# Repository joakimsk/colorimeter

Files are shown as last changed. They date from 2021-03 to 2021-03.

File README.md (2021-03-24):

# Colorimeter

A project to develop an open source colorimeter that is "good enough". End goal is to analyze sample colors for water quality measurements, using off-the-shelf test kits for aquarium water quality. In the process, maybe we can do a sample with less reagents, as well.

Photometer: Measuring quantity of light, usually all kinds of wavelengths, "full spectrum". Output is light intensity.

Colorimeter: Measures the absorbance of particular wavelengths of light by a specific solution. Normally, only a narrow wavelength, where most light is absorbed by the solution, selected with filters is used to maximize accuracy, and Beer-Lambert law is applied to deduce the solution strength.

Spectrophotometer: Measures the absorbance across several wavelengths of light, giving a graph of spectral absorption. Like a colorimeter but across many wavelengths.

I believe this means that we could manage with a single "full-spectrum" light measurement of the liquid, but it gets more accurate as we select correct wavelength. A spectrophotometer is more fancy than necessary in our case.

If our solution will be green to blue, we want a light source that is in between green and blue, depending on where we want best accuracy.

Read the [NOTES.md](NOTES.md) for more details and testing.

## What you need
### Hardware needed
- An LDR, light sensitive resistor as light detector
- A single-wavelength or multi-wavelength LED as light source
- A couvette, preferably of quartz due to its optical qualities (Mine is 12.5x12.5x45mm from Purshee.com wavelength 200-2500nm, 3.5ml volume)
- An Arduino to make the measurements
- A PC to run software and analysis

### Tools needed
- A 3D-printer is nice but not necessary, print in black filament if possible, reduce light noise. Or spray paint with black. Or run in dark room.
- A PC for software
- Basic electronics tools are recommended

### Other things needed
- Food coloring for initial tests (optional)
- Water quality test kit (ammonia suggested, can be of any chemistry, but I am using salicylate method, JBL Seawater Ammonia test kit)
- Household ammonia (to calibrate software)
- A small syringe, I have 1 ml with a short tip from the local pharmacy

## Theory
Send light through a liquid, our sample. Detect how much light is received. With light at a certain color, the light received tells us how much light was absorbed, and how much was passed through the sample. If we use three different colors, maybe we can say which color the liquid is.

By taking samples through time, we can explore the kinematics of the liquid, to make sure we make a reading we can trust, when reagents are done reacting.

Putting this all together, we can also calibrate the readings of the kits to a known solution, for example using an ammonia kit and dosing ammonia at certain concentrations.

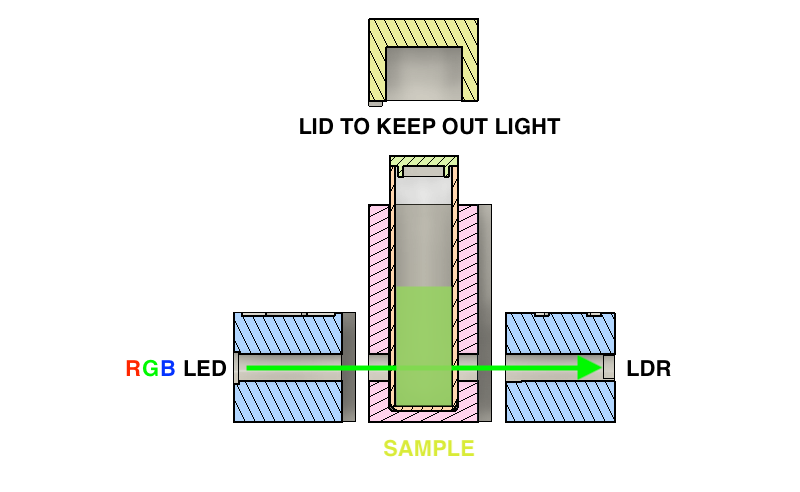
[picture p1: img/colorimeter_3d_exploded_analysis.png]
Light path

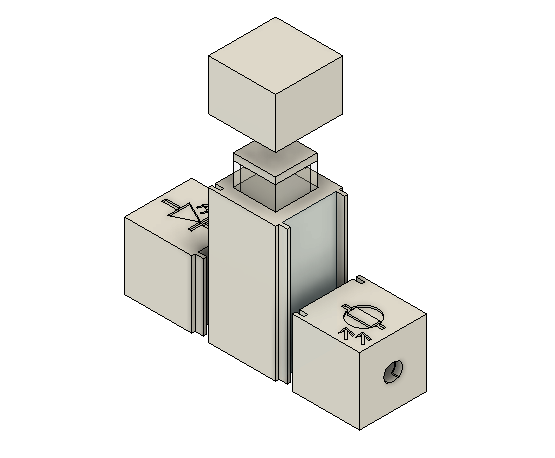
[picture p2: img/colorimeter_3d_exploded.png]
Overview of couvette holder


Something like that.

### Optical parameters
Reflectance: Amount of reflected light, referenced to a reference measurement. Expessed in % or dB, negative number.

Absorbance: Amount of light absorbed, referenced to a reference measurement, can be original light source. Expressed in dB, considered opposite of transmittance.

Transmittance: Amount of light transmitted through a liquid, referenced to a reference measurement, can be original light source. Expressed in % or dB.

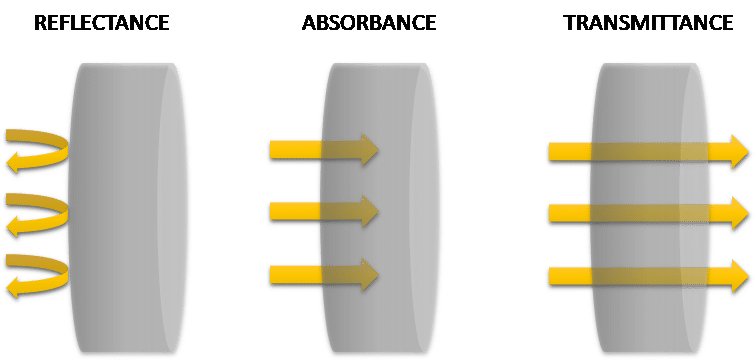
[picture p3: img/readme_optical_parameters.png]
Optical parameters, copyright original owner


[pyroistech.com relative measurements ](https://www.pyroistech.com/relative-measurements/)

We should probably decide on what 100% transmittance is, then do a divison to find relative transmittance for various colors/wavelengths.

[sigmaaldrich.com transmittance/absorbance table](https://www.sigmaaldrich.com/technical-documents/articles/biology/transmittance-to-absorbance.html#:~:text=Absorbance%20(A)%20is%20the%20flip,be%20determined%20using%20this%20calculator.)

### Beer-Lambert law
[wikipedia.org Beer-Lambert law](https://en.wikipedia.org/wiki/Beer%E2%80%93Lambert_law)

Related to the attenuation of light, as it passes through a material. Absorbance = absorpitivity * optical path in cm * concentration of attenuating species.

Should only be applied to absorbance within 0.2 to 0.5, to maintain linearity.

## LDR details
The LDRs are commonly of CdS, Cadmium sulfide. They have also been mostly discontinued on Elfa Distrelec, but I found a datasheet.

They are most sensitive to green wavelengths, which may explain blue and green samples giving nearly the same, high response.

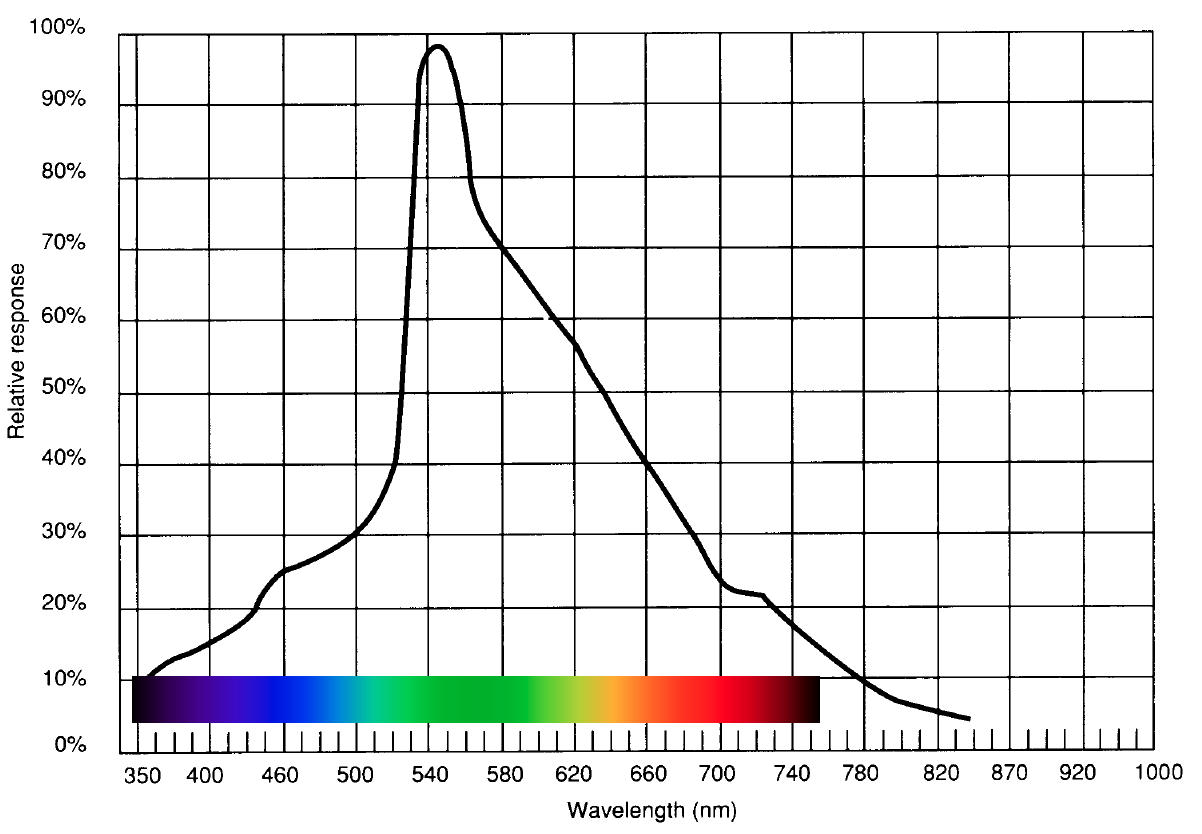
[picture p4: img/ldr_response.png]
LDR spectral response

[pdf: ldr datasheet](pdf/ldr_datasheet.pdf)

## Quartz couvette details
The couvettes are often found in plastic, normal glass and quartz glass. There are various types of quartz, suitable for different wavelengths.

Here is a typical UV Quartz couvette transmittance plot, very transmissive from 200 to 2000 nanometers, far beyond visible light.

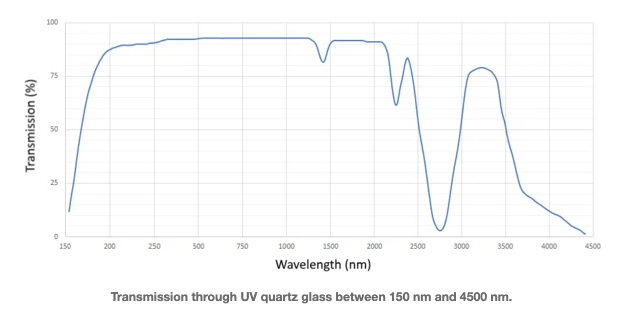
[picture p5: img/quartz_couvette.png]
Quartz couvette Quartz


## Error sources
- If using a round couvette (glass vials that follow test kit), light can get bent along sides and avoid the liquid all-together. Thus we do not use the vials, for now.

- If using a small reagent dose, we may get imbalance in chemistry. Not sure how this will affect the reading. Read up on best practice with syringe usage.

- White PLA plastic, and 20% infill during print will allow more light to pass through the body. And, imperfect joints will too. Try black plastic spray paint for this. If not enough, use black PLA and set 100% infill. If still not enough, put it all inside another light-proof box.

- LDR and LED may not be accurate enough, so we may consider upgrading these components, maybe using a light sensor instead of a light resistor. LDR resistance is among other, temperature dependent. LDR has also a bit of latency, it takes time for the resistance to reach stable value, going from full dark to full light, often taking one second.

- Conversion roundoff errors and noise in Arduino may become a problem as well. Arduino Uno is 8 bit, the ADC has 8 bit resolution. The LDR is an analog device.

- Temporal issues due to sampling not being instant - if we make several readings at several colors, these will necessarily happen at a delta t larger than 0. Meaning that our readings will not happen in the same time, but spread over time, giving us small errors. By making sampling faster, we can mitigate but not eliminate this. Using a full spectrum light and read all wavelengths at the same time would be the best, but most expensive.

## Remaining work
- ~~Design 3D models, then print for couvette-assembly~~
- ~~Assemble electronics~~
- ~~Make Arduino software~~
- Make PC software (in progress)
- Test and calibrate (in progress)
- Final casing

## Final thoughts
The idea of the colorimeter works well, but there are some numbers of improvements I suggest for the future.

- The LDR is undocumented, and delays the whole sampling process, since it takes time for it to settle when light exposure changes. Get a phototransistor or a color sensor or similar.
- The RGB led is undocumented as well as lacking a "full spectrum" white color. Preferably it is replaced with well documented light sources, or as in professional instruments, with color filters on a natural light source.
- The 3D-printed casing should be printed in black plastic, fully filled, to avoid light leakage.
- The modularity is not necessary, so consider printing it all in one print.
- The quartz couvette is overkill, it seems, can potentially manage well with normal glass couvettes, or even plastic, due to calibration.
- The arduino programmed as a simple device works well, with program logic in python.
- The color standards should be more standard, food coloring works to get an impression but it still do not seem very standard, at least not without measuring exactly. Also, maybe we do not need standards anyhow, after designing this system.
- There should be a couvette holder nearby, at all times, to avoid spilling water all over the place. I suggest printing this as an addon.
- Using wood as a base works well, with glue gun to keep things together.
- Using a small couvette with lesser volume makes you depend on an exact syringe - get an exact robust syringe, not cheap one that loose its markings over time.
- Making one that fits aquarium test vials may be nice, one for JBL, one for 

## Theory & code references
[moleculardevices.com Absorbance](https://www.moleculardevices.com/technology/absorbance)
[electronics-tutorials.ws Light sensors](https://www.electronics-tutorials.ws/io/io_4.html)

## Similar work
[mit.edu Low Cost Colorimeter](http://www.mit.edu/~milesdai/projects/colorimeter/index.html)
[iorodeo.com Open Source Colorimeter Project](https://iorodeo.com/pages/colorimeter-project)
[instructables.com Inexpensive photometer & colorimeter](https://www.instructables.com/An-Inexpensive-Photometer-and-Colorimeter/)
[arduino.cc Open Source Colorimeter](https://create.arduino.cc/projecthub/MOST/open-source-colorimeter-cd0a76)
[arduino.cc Mini spectrophotometer](https://create.arduino.cc/projecthub/radsensors/minispec-0e3bc5)
[publicLab.org Desktop spectrometer with DVD diffraction grating](https://publiclab.org/notes/abdul/08-11-2016/constructing-a-desktop-spectrometer-with-no-wood-and-no-velcro)

[researchgate.net A Simple, Rapid Analysis, Portable, Low-cost, and Arduino-based Spectrophotometer with White LED as a Light Source for Analyzing Solution Concentration](https://www.researchgate.net/publication/324161531_A_Simple_Rapid_Analysis_Portable_Low-cost_and_Arduino-based_Spectrophotometer_with_White_LED_as_a_Light_Source_for_Analyzing_Solution_Concentration)
[researchgate.net Open-Source Colorimeter](https://www.researchgate.net/publication/236252679_Open-Source_Colorimeter/link/0c9605171839574c56000000/download)
[iop.org Development of color detector using colorimetry system with
photodiode sensor for food dye determination application](https://iopscience.iop.org/article/10.1088/1742-6596/1185/1/012031/pdf)

## Possible light sources and detectors
[sparkfun rgb light sensor ISL29125](https://www.sparkfun.com/products/12829)
[Digital 16bit Serial Output Type Ambient Light Sensor IC BH1750FVI](https://www.mouser.com/datasheet/2/348/bh1750fvi-e-186247.pdf)
[electronics-notes.com LDR: Light Dependent Resistor](https://www.electronics-notes.com/articles/electronic_components/resistors/light-dependent-resistor-ldr.php)

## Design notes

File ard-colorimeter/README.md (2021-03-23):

# ard-colorimeter
Arduino program to interface with colorimeter

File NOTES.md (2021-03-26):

# Colorimeter Notes
## PWM vs LDR resistance

Measurement of LDR resistance against PWM output value, Arduino ADC range is {0-255}. Shining through the colorimeter, but without couvette (i forgot it...).
Colorimeter is kept in the dark (with a Norwegian dark grey lue), so light pollution should be minimal.

|       	| 20     	| 45    	| 50    	| 100  	| 150  	| 200  	| 250  	| 255  	|
|-------	|--------	|-------	|-------	|------	|------	|------	|------	|------	|
| Red   	| ~1975k 	| ~835k 	| ~760k 	| 366k 	| 241k 	| 180k 	| 144k 	| 142k 	|
| Green 	| 526k   	| 232k  	| 208k  	| 102k 	| 67k  	| 49k  	| 38k  	| 38k  	|
| Blue  	| ~760k  	| 333k  	| 299k  	| 141k 	| 88k  	| 63k  	| 49k  	| 48k  	|
| All   	| 249k   	| 112k  	| 101k  	| 50k  	| 32k  	| 23k  	| 18k  	| 18k  	|

All means all three colors are turned on at the same time. Driving voltage is 5v, and resistors I forgot to write down...

We do this to consider which resistor value to use for the voltage divider on the LDR side.

We also get an impression of where the LDR is most sensitive, and least sensitive.

Here is a chart of the data.

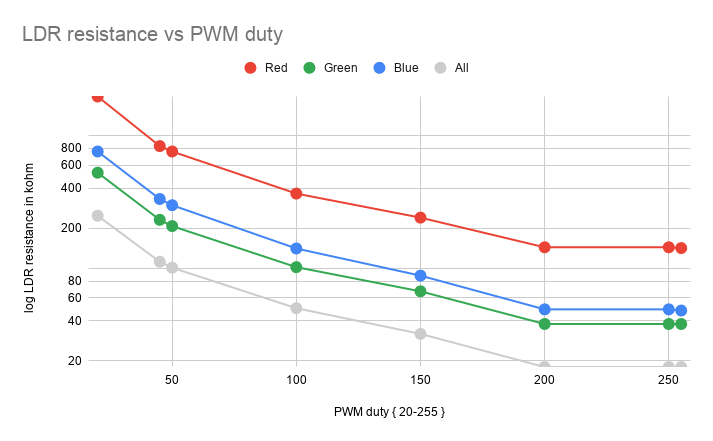
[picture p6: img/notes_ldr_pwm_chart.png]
Light path LDR vs PWM duty chart


Average of the table is 256.9 kohm
Median of the table is 126.5 kohm

I cannot remember how to select optimal value, so I will just use the average value as the second resistor in the voltage divider. This should give us a 2.5 volt to ADC when the LDR is at the average value.

I select 220 kohm + 38.6 kohm, measured to 258 kohm, near enough to 256.9 kohm.

We set RGB to <100,100,100>
LDR resistance with clear path: 53 kohm
LDR resistance with quartz couvette: 58.3 kohm and inserted wrongly: 191 kohm
LDR resistance with plastic couvette: 61 kohm and inserted wrongly: 66 kohm

## Thoughts about Arduino ADC
The Analog to Digital conversion in the Arduino Uno, using the ATmega328 8-bit MCU, has 10 bits resolution.

ADC Resolution = Vref / ((2^n) - 1) = 5 / ((2^10)-1) = 5/1023 = 0.00488758553 volt bins

Digital output = Vin / Resolution
Digital output = 5 / 0.00488758553 = 1023 (when Vin is 5v)
Digital output = 2.5 / 0.00488758553 = 512 (when Vin is 2.5v)

A voltage divider:
Vout = ( R2 / (R1 + R2)) * Vin
Vout = ( R2 / (R1 + R2)) * Vin

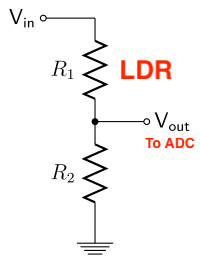
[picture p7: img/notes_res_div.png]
Light path Resistive divider


Setting R2 = 258 kohm
We have R1 being the LDR, varying from 18 kohm to up to 2000 kohm (guestimates finger in the air values from the table).

We set R1 to be LDR because when LDR gets light on it, it will "pull up" Vout to Vin voltage. This is because LDR resistance goes down when light amount goes up.

This gives us two extremes, for high light and low light conditions, remembering that the LDR lowers resistance under higher light:

Vout = ( 258000 / (18000 + 258000)) * 5 = 4.67391304348 volts

Digital output = 4.67391304348 / 0.00488758553 = 956 (when Vin is 5v)

Vout = (258000 / (2000000 + 258000)) * 5 = 0.5713020372 volts

Digital output = 0.5713020372 / 0.00488758553 = 117 (when Vin is 5v)

## Color sample solutions
Food coloring was used to make "standard" solutions for red, green and blue. The primary colors we are interested in, for the Salicylate method for total ammonia nitrogen, is green/yellow to dark blue, but it is nice to check the colorimeter for more colors.

"1 cm long" string of blue food coloring and 5 ml freshwater was mixed.
Aproximately the same amount of red and green was added to their own 5 ml freshwater, and was mixed.

Two "1ml syringes" of colored liquid was added to the quartz couvettes, totalling 2 ml in each couvette, hopefully enough to not allow light to pass in air above the liquid.

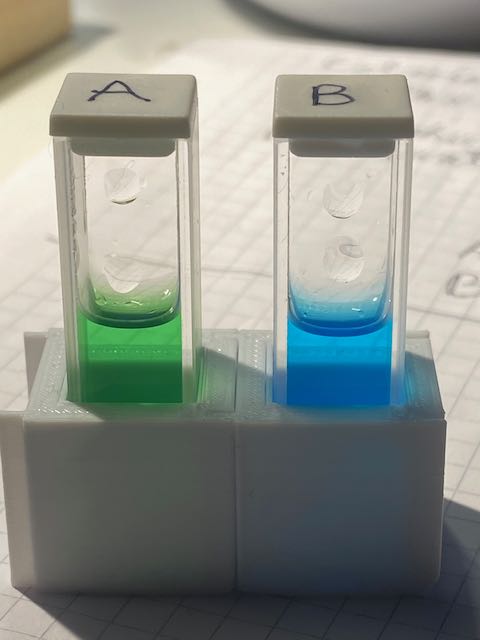
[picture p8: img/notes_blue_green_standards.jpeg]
Blue & Green Blue & Green Standard

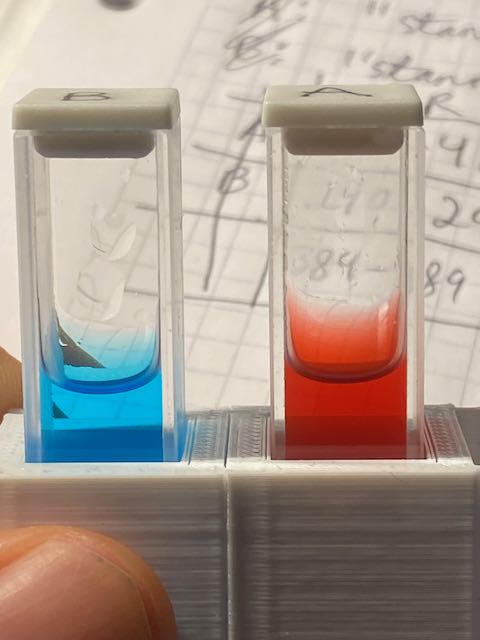
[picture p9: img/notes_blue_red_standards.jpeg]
Blue & Red Blue & Red Standard


## Actual LED colors
It seems that R + G + B != White with an RGB led, to my eyes it looks more azure blue than anything else.
Ideally I would do all this with a white LED as well one day.

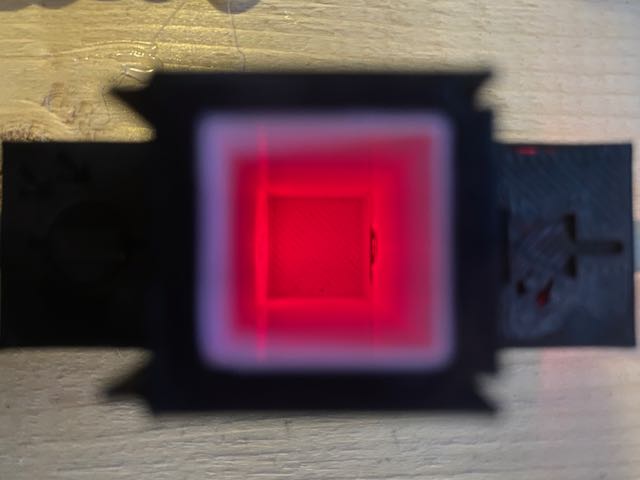
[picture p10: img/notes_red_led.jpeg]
Red Red led

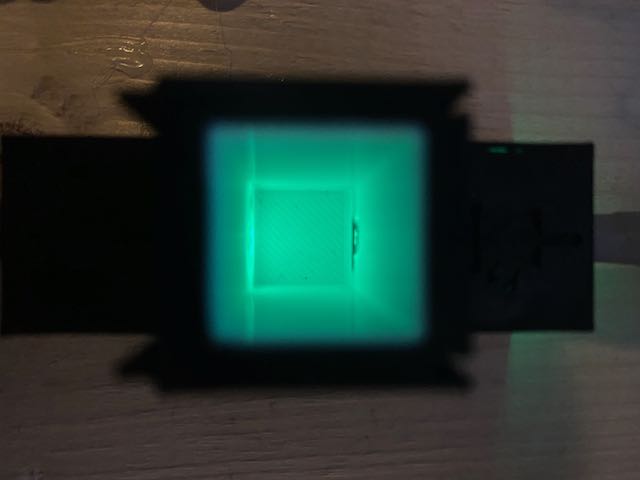
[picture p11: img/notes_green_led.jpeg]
Green Green led

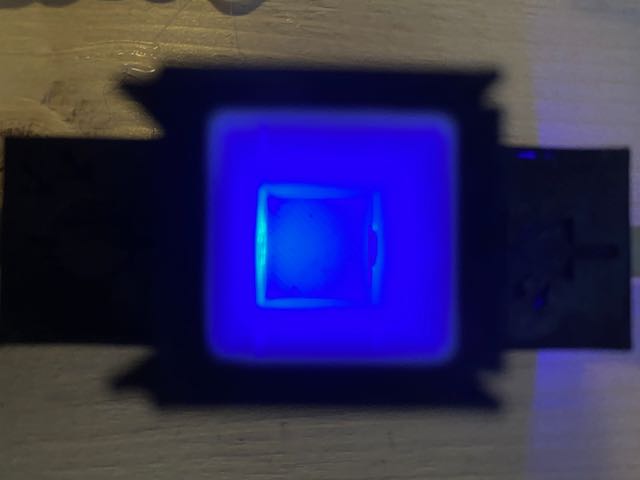
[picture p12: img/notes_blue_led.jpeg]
Blue Blue led

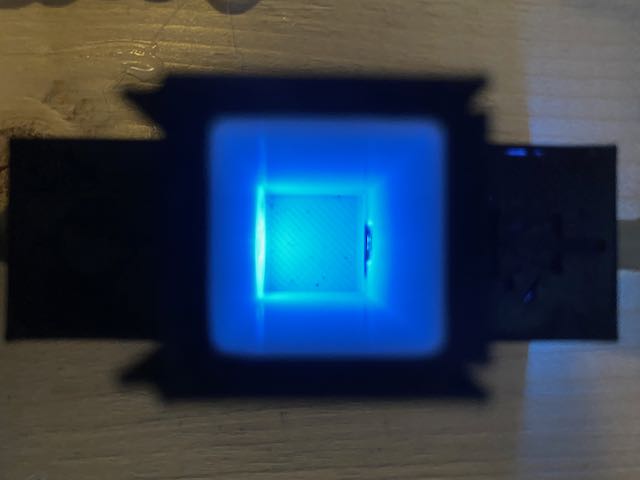
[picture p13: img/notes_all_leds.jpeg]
All All leds


## First trials
We receive the voltage coming from the voltage bridge, using an ADC in the Ardunio, translating this voltage into a value between 0-1023.

We use the "Lue" to make sure its dark around the colorimeter, as the black spray paint was not enough to make it opaque to outside light.

This is just to get to know the thing. Lids of couvettes were marked A and B, to keep them seperate. A couvette stand was used after the first spill of saltwater across the desk.

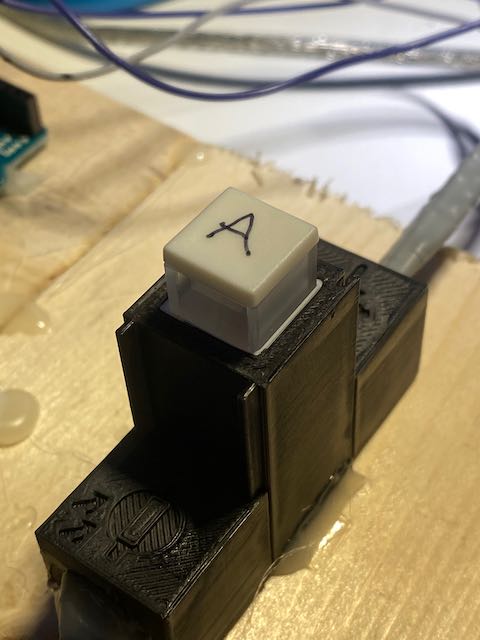
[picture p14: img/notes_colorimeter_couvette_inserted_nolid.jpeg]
Colorimeter, couvette inserted


### Comparing freshwater and saltwater without and with lue
Temperature on both water was roughly 10 degree Celsius in this case. I forgot to make readings with all LEDs on.

Unit: 10-bit ADC values, higher means more light passed liquid
|                  | R       | G       | B       | All |
|------------------|---------|---------|---------|-----|
| Freshwater       | 706-710 | 909-910 | 885-886 | NA  |
| Saltwater        | 703-704 | 906-907 | 882-883 | NA  |
| Freshwater (Lue) | 705-708 | 907-909 | 882-883 | NA  |
| Saltwater (Lue)  | 705-707 | 906-907 | 881-882 | NA  |

Here I wanted to see if Lue had much to say on the readings. It has 1-4 values to say, it seems, so we continue using Lue.
I also think freshwater and saltwater has different colors, but the readings fluctuate a bit so not so easy to say.

### Comparing "standard" freshwater solutions
The "standards" were compared.

Unit: 10-bit ADC values, higher means more light passed liquid
|                    | R       | G       | B       | ALL     |
|--------------------|---------|---------|---------|---------|
| "Standard green"   | 408-412 | 869-870 | 550-553 | 900-902 |
| "Standard blue"    | 290-294 | 891-892 | 879-880 | 950     |
| "Standard red"     | 384-389 | 0-1     | 0-1     | 373-376 |
| "50% standard red" | 566-568 | 48-51   | 141-145 | 612-614 |

It seems that the "standard red" is too dense, it does not allow any green nor blue through it. After diluting 50%, it was better, but still very strong. I believe the standard was mixed too strong.

Here is blue, red and 50% red standards, notice transparency and lack thereof.

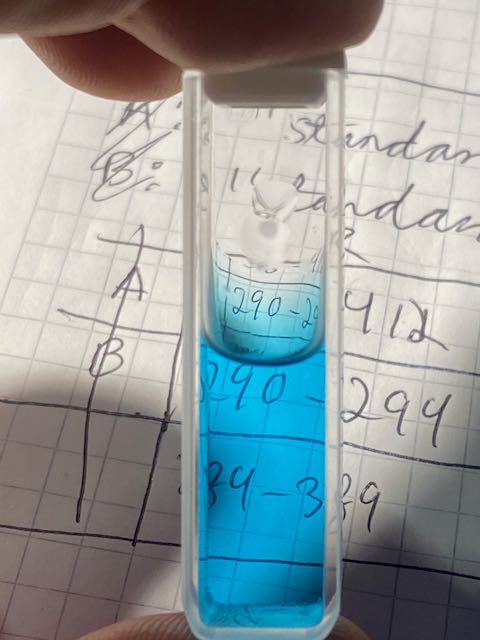
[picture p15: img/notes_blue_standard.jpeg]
Blue standard

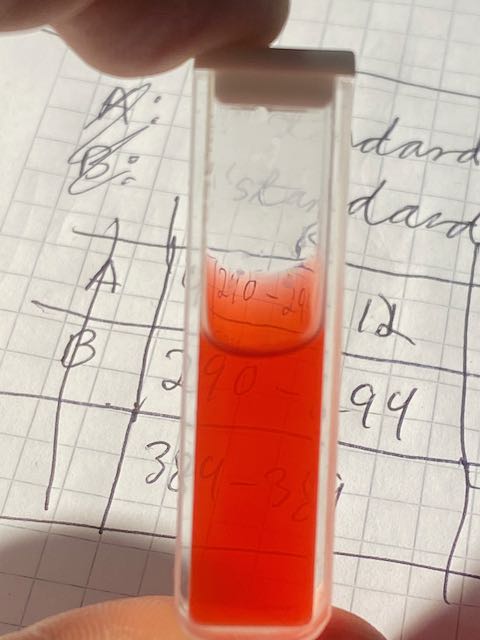
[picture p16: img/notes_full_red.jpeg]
Red standard

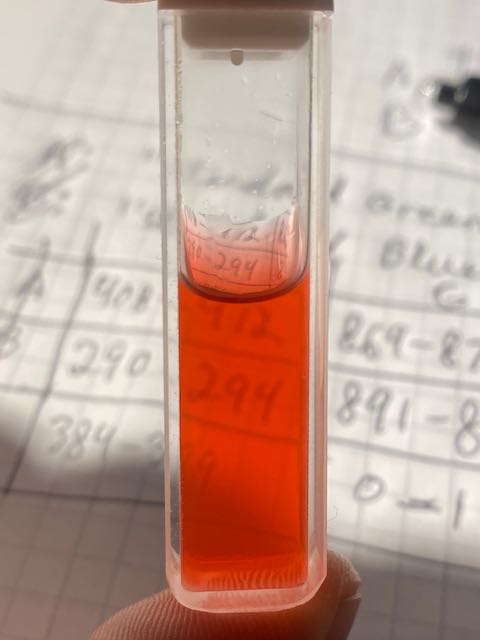
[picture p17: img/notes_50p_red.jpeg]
50% red standard


### Some observations, possible issues and improvements
There is a big difference in viscosity between red, green and blue food coloring. The blue was very viscous, and it was difficult to portion out the amount of coloring by volume

When sampling, I would say I used "n=5-10" by making several reads after a few seconds, when LDR should be stable, not so scientific.

Saltwater vial also had small bubbles in it, which may reduce light. And, try to avoid touching the quartz with my fatty fingers.
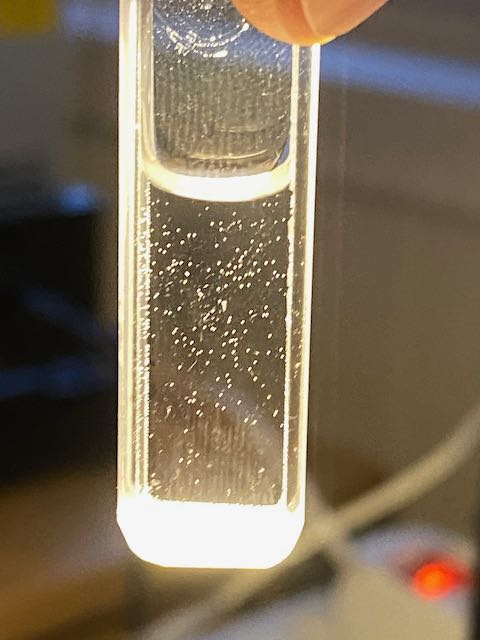
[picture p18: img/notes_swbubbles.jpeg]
Bubbles in saltwater


Pharmacy syringes seem to loose their markings after some mechanical action. Get a proper one.

The LDR likely does not behave linearly, either.

The voltage divider would probably be nicer with a potentiometer, so we can adjust the voltage range.

### Conclusion from first trials
Red is more opaque to green and blue, than red light.
Green is more opaque to blue and red, than green light.
Blue is more opaque to green and red, than blue light.

Could we use ALL leds without a couvette as 100% Transmittance, and then do a simple divison to find transmittance in %? Plausible way forward.
We could also do transmittance at different wavelengths.

## Transmittance implementation
I think we can do this naively, take a calibration reading with an empty couvette in the colorimeter.

Then, take another with the couvette filled with sample liquid, and do a division of ADC values. Output in % transmittance, according to the different LED colors.

Since we do a calibration reading, we should even be able to let the Lue be on the head, where it belongs, instead of on top of the colorimeter.

## LDR time stability and settling-time
It seems that one second is not enough for the LDR to settle after being illuminated. I should probably try an experiment for each LED, to see how long the LDR really takes.

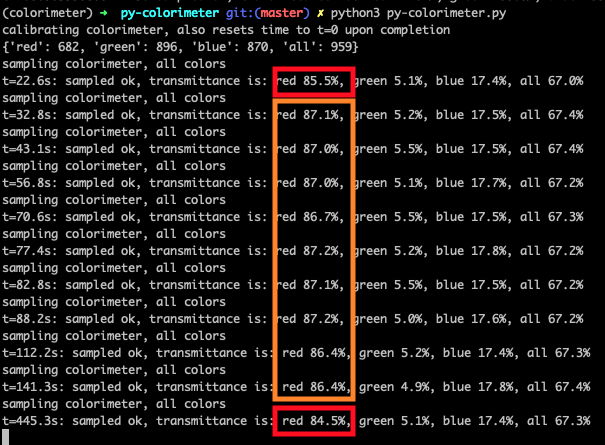
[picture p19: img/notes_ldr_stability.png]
LDR time stability


Notice that after the LDR has been kept in the dark for a while, the end-point does not seem to be reached, since the red-transmittance reading is lower.

Since my LDR is a generic no-name without a datasheet, I have no clue about its spectral response nor its response time, but response time could be deduced experimentally.
My RGB led is also generic no-name, without a datasheet.

[lednique.com ldr details](http://lednique.com/opto-isolators-2/light-dependent-resistor-ldr/)

## Test methods

There are a few different methods, and variations of those used to measure total ammonia nitrogen, TAN, in aquaculture. The goal is to figure out if we have toxic levels of unionized ammonia NH3 in the water, but the test kits have a tendency to be ambigous regarding what they are actually indicating.

Two of the more common ones in the hobbyist aquarium world is:

The Salicylate method. In the salicylate method, monochloramine formed by the reaction of ammonia and hydrochlorine reacts with salicylate to form blue-green colored 5-aminosalicylate in proportion to the amount of ammoniacal nitrogen. Works well on lower concentrations of TAN, commonly 0–1.0 mg/L.

The Nessler method. A combination of mercury (II) iodide and potassium iodide in highly alkaline solution. Gives a yellow color. Contains mercury, and is thus not available in Norway. Also has a wider effective undiluted range of 0.02–5.0 TAN.

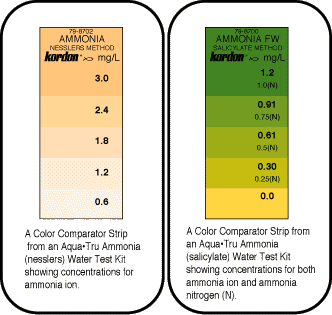
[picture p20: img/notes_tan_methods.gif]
Salicylate vs Nessler

Read more about these two [here](https://aquabaz.tripod.com/ammoniageneral.htm)

And a more detailed comparison of several methods [Comparison of Nessler, phenate, salicylate and ion selective electrode procedures for determination of total ammonia nitrogen in aquaculture](https://www.sciencedirect.com/science/article/abs/pii/S0044848615301058)

On the topic of units, Nofima has a nice writeup in Norwegian. [Here](https://www.nofima.no/filearchive/produksjon-og-giftighet-av-ammoniakk.pdf)

TAN = NH3-N + NH4+-N

Total Ammoniacal Nitrogen = Ammonia-Nitrogen + Ammonium-Nitrogen

This means we are looking at the ammount of nitrogen.

These two parts of TAN exists in a pH-related equilibrium.

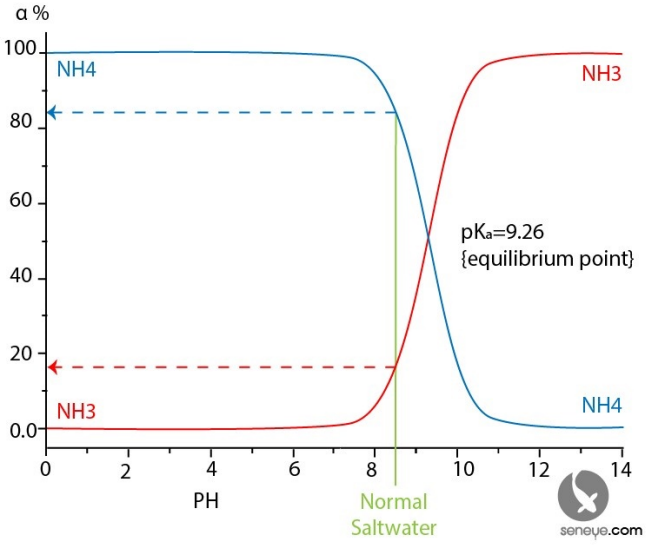
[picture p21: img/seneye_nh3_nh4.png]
NH3 vs NH4


In RAS operating range, we may find pH from 7 to about 8.1, normal seawater.

Calculate Free Ammonia using [Hamza Reef Free Ammonia calculator](https://www.hamzasreef.com/Contents/Calculators/FreeAmmonia.php)

You can also see the [nitrogen-ion conversion chart](https://www.hamzasreef.com/Contents/Calculators/NitrogenIonConversion.php)

## JBL NH4 test kit
The JBL NH4 test kit is used for measuring ionized NH4+, or so they say. I think they actually indicate TAN. The values are indicated to be mg/l or ppm, ranging from below 0.05 to 5.

The chemistry used in this is the Salicylate method, which means the colors we will see range from a light green to dark blue, depending on the ammonia concentration.

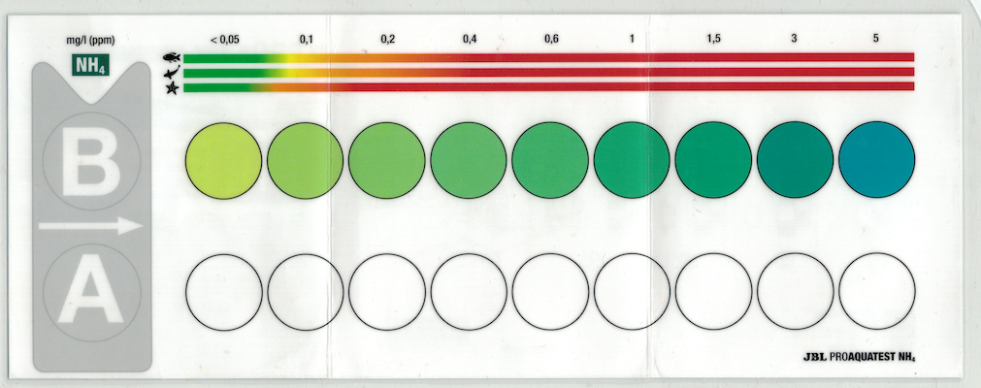
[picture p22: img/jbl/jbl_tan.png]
JBL TAN color sheet


Indicated colors are of the following "NH4", or I believe, TAN.
| Concentrations: 	| <0.05 	| 0.1 	| 0.2 	| 0.4 	| 0.6 	| 1 	| 1.5 	| 3 	| 5 	|
|-----------------	|-------	|-----	|-----	|-----	|-----	|---	|-----	|---	|---	|

The price is roughly 200 NOK, and you get 50 tests out of it if you follow the normal procedure.

The normal procedure is:
1. Add 5 ml water to be measured to a vial
2. Add 4x drops of Solution #1
3. Add 4x drops of Solution #2
4. Add 5x drops of Solution #3
5. Wait 15 minutes, for reaction to take place
6. Compare color of liquid to color indicated on test sheet

Remember that when we measure TAN, we have no idea how much is of the toxic unionized NH3 and how much is of the less toxic ionized NH4+.
To figure out this, we also need to look at the pH and possibly salinity and temperature as well, 

## Ammonia solutions

In order to test our colorimeter, with the JBL NH4 test kit, we need to make a few standard solutions.

We have 9% NH4Cl, Ammonium Chloride, unperfumed from the store.

For 100 liters of water, elevating it from 0 to 1 mg/L TAN, using 9% Ammonium Chloride, and a (calculator)[http://spec-tanks.com/ammonia-calculator-aquariums/].

We need to add 1.1 ml Ammonium Chloride solution.

This is for 1 liter of water, 0.011 ml Ammonium Chloride, too little for me to measure with my 1 ml syringe.

We can take a bucket of 20 liter, add 0.2 ml Ammonium Chloride and get a 1 mg/L solution.
We can take a bucket of 20 liter, add 1.1 ml  ml Ammonium Chloride and get a 5 mg/L solution.

We should also dilute us down to a few different ones.

I have 1 mg/L solution on hand, so I use this and make one more at 0.5 mg/L, by mixing 50/50 of water and solution.

To do later: Make a more complete table, so that we can make better tests.

## TAN kinetics

I put together autosampling, interval of 30 seconds, for 15 minutes. First tests with the real JBL TAN test kit.

Seawater of 1 mg/L TAN, at room temperature (ca 20 degree Celsius):
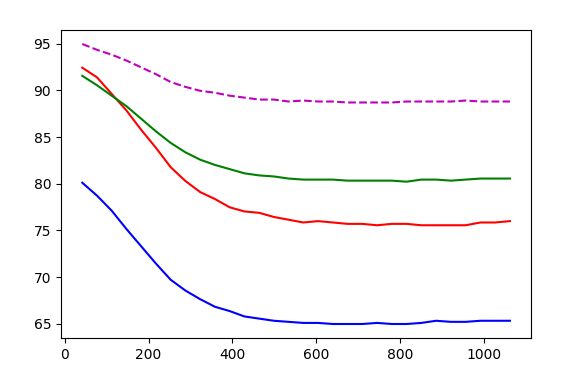
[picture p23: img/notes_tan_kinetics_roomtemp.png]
TAN kinetics room temp


Seawater of 1 mg/L TAN, at fridge temperature (ca 4 degree Celsius):
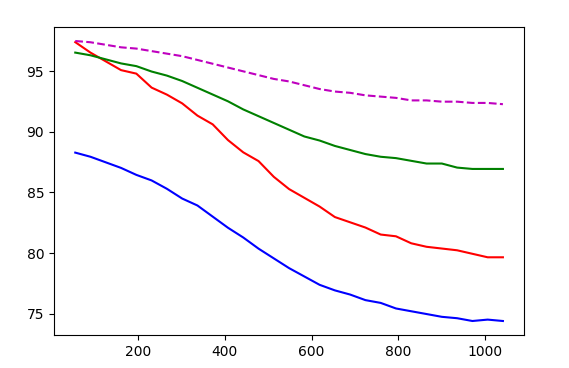
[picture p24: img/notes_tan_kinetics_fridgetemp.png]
TAN kinetics fridge temp


Seeing these side by side, we can clearly see that the cold one takes longer to react fully.

We also see that, after the procedure, waiting 15 minutes gives us end values that are not the same. This means, as far as I can tell, that the color is different.

First line of roomtemp:
t=41.7s: sampled ok, transmittance is: red 92.4%, green 91.6%, blue 80.1%, all 95.0%

Last line of roomtemp:
t=1062.0s: sampled ok, transmittance is: red 76%, green 80.6%, blue 65.3%, all 88.8%%

First line of chilled:
t=55.5s: sampled ok, transmittance is: red 97.4%, green 96.5%, blue 88.3%, all 97.5%

Last line of chilled:
t=1040.9s: sampled ok, transmittance is: red 79.7%, green 86.9%, blue 74.4%, all 92.3%

## 50% of 1 mg/L TAN test

I diulted the 1 mg/L solution down to 0.5 mg/L and did another plot over 15 minutes.

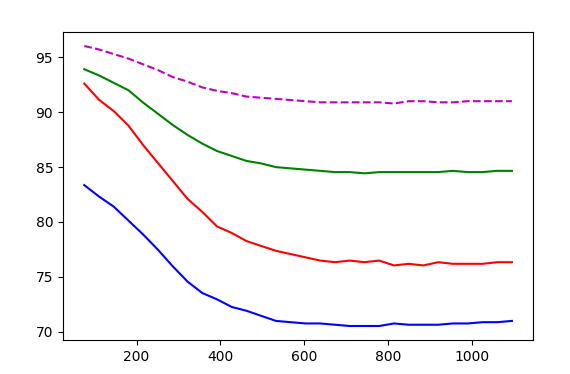
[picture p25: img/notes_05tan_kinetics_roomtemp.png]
TAN kinetics room temp for 0.5mg/L TAN


First line of 0.5 mg/L at room temp:
t=75.2s: sampled ok, transmittance is: red 92.6%, green 93.9%, blue 83.4%, all 96.0%

Last line of 0.5 mg/L at room temp:
t=1095.5s: sampled ok, transmittance is: red 76.3%, green 84.7%, blue 71.0%, all 91.0%

Note that the transmittance difference of the green and blue was most significant.

1 mg/L TAN: 79.7% red, 86.9% green, 74.4% blue

0.5 mg/L TAN: 76.3% red, 84.7% green, 71% blue

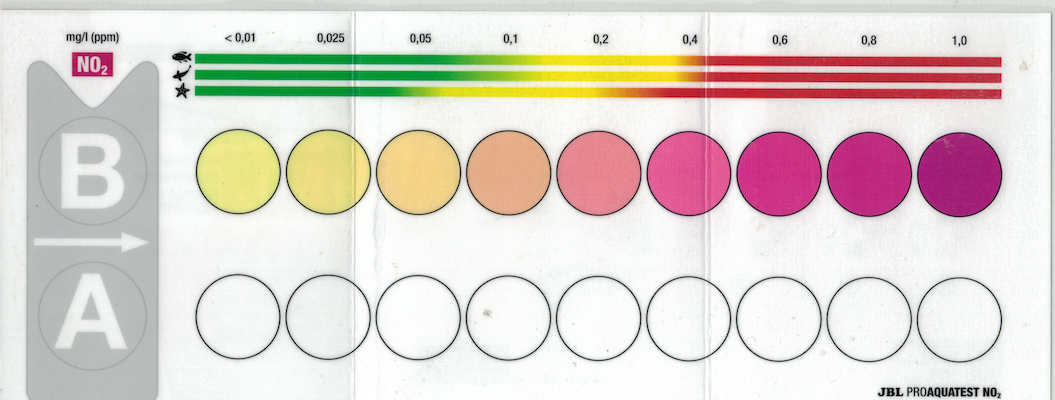
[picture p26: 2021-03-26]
img/jbl/jbl_no2.png

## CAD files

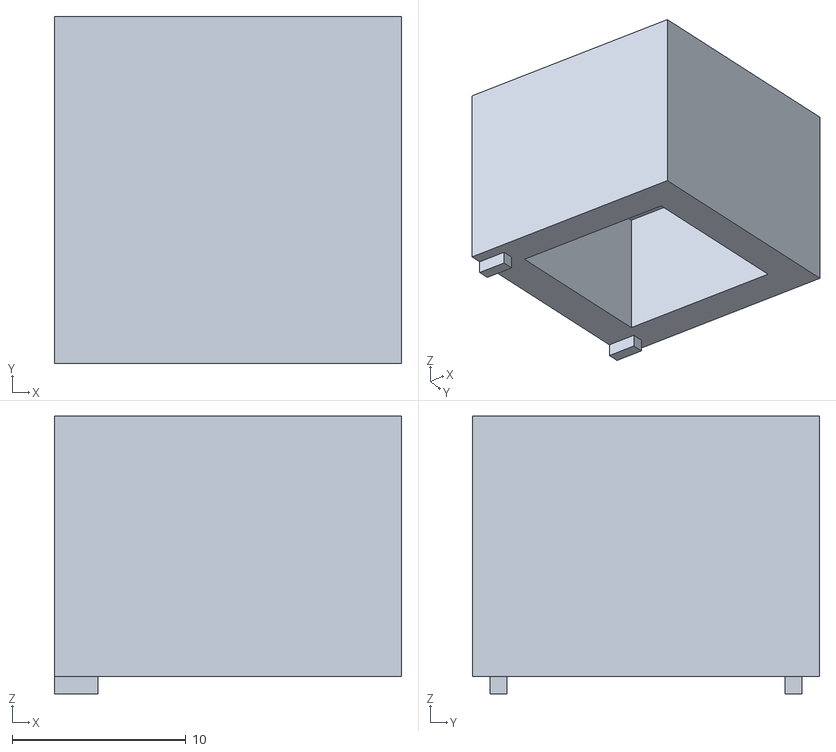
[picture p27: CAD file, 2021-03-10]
3d-stl/Couvette Holder Lid.stl
20.0 x 20.0 x 16.0

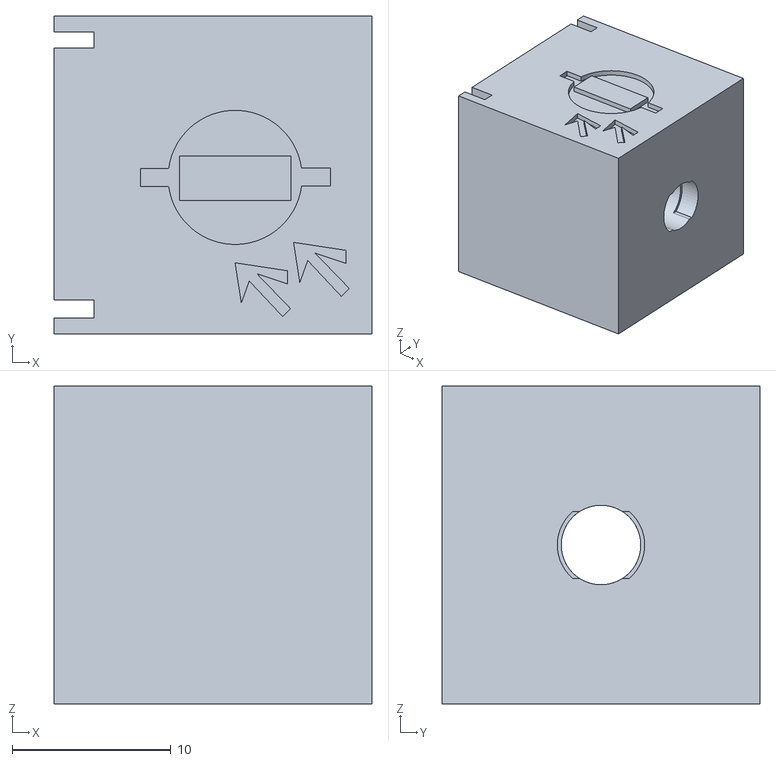
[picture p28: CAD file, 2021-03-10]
3d-stl/LDR holder.stl
20.0 x 20.0 x 20.0

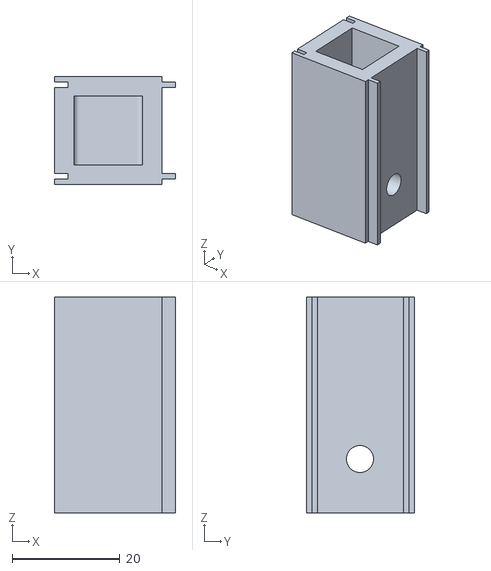
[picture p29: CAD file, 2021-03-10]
3d-stl/Couvette Holder.stl
22.5 x 20.0 x 40.0

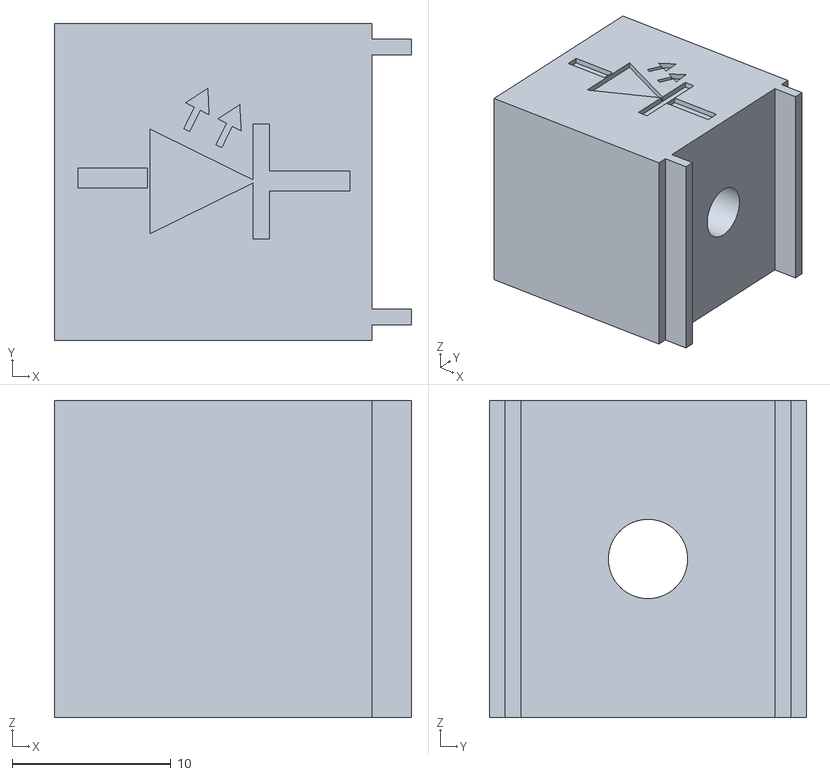
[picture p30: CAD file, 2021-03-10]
3d-stl/LED holder.stl
22.5 x 20.0 x 20.0

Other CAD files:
3d-projects/Couvette Holder v20.f3z
3d-projects/Quartz Couvette v1.f3d

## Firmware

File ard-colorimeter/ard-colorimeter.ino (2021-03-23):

#include <ArduinoJson.h>
#include <MovingAverage.h>

// Prototypes in header
#include "ard-colorimeter.h"

#define ledRedPin 9 // red
#define ledGreenPin 10 // green
#define ledBluePin 11 // blue
#define ldrPin 14 // A0

uint16_t ldrVal = 0; // 2 bytes unsigned int, 0-65535

MovingAverage <uint16_t, 8> filter;
StaticJsonDocument<200> jsonOut;

const byte numChars = 32;
char receivedChars[numChars];
char tempChars[numChars];

char messageFromPC[numChars] = {0};
int redPwmFromPc = 0;
int greenPwmFromPc = 0;
int bluePwmFromPc = 0;

boolean newData = false;

int invertvalue(int inval){
    return 255-inval;
}

void setPinPwm(int redPwm, int greenPwm, int bluePwm){
    analogWrite(ledRedPin, invertvalue(redPwm));
    analogWrite(ledGreenPin, invertvalue(greenPwm));
    analogWrite(ledBluePin, invertvalue(bluePwm));
}

void setup() {
    Serial.begin(9600);
}

void loop() {
   recvWithStartEndMarkers();
   if (newData == true) {
       strcpy(tempChars, receivedChars);
            //this temporary copy is necessary to protect the original data
            //  because strtok() used in parseData() replaces the commas with \0

       parseCommand();
       newData = false;
   }

    ldrVal = analogRead(ldrPin);
    filter.add(ldrVal); // Add to moving average filter, 8 values
    
    delay(1); // delay 1 ms per cycle
}

void recvWithStartEndMarkers() {
    static boolean recvInProgress = false;
    static byte ndx = 0;
    char startMarker = '<';
    char endMarker = '>';
    char rc;

    while (Serial.available() > 0 && newData == false) {
        rc = Serial.read();

        if (recvInProgress == true) {
            if (rc != endMarker) {
                receivedChars[ndx] = rc;
                ndx++;
                if (ndx >= numChars) {
                    ndx = numChars - 1;
                }
            }
            else {
                receivedChars[ndx] = '\0'; // terminate the string
                recvInProgress = false;
                ndx = 0;
                newData = true;
            }
        }

        else if (rc == startMarker) {
            recvInProgress = true;
        }
    }
}

void parseCommand() {

  char *strtokIndx; // this is used by strtok() as an index

  switch (tempChars[0]) {
  case 'r': //read ldr ex <r>
    Serial.println(filter.get());
    break;
  case 's': //set leds ex <s,{rgb},255>
    strtokIndx = strtok(tempChars, ","); // jump over the command
    strtokIndx = strtok(NULL, ",");
    char *color = strtokIndx;
    if (strcmp(color, "r") == 0){
        strtokIndx = strtok(NULL, ",");
        redPwmFromPc = atoi(strtokIndx);     // convert this part to an integer
    } else if (strcmp(color, "g") == 0){
        strtokIndx = strtok(NULL, ",");
        greenPwmFromPc = atoi(strtokIndx);     // convert this part to an integer
    } else if (strcmp(color, "b") == 0){
        strtokIndx = strtok(NULL, ",");
        bluePwmFromPc = atoi(strtokIndx);     // convert this part to an integer
    } else {
        Serial.print("Unknown color:");
        Serial.println(color);
    }
    setPinPwm(redPwmFromPc, greenPwmFromPc, bluePwmFromPc);
    break;
  default:
    Serial.print("Unknown command: ");
    Serial.println(tempChars[0]);
  }
}

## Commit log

2021-03-10 skeleton folders added
    [Couvette Holder Lid.stl, Couvette Holder v20.f3z, Couvette Holder.stl, LDR holder.stl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]
2021-03-20 Initial arduino commit
2021-03-20 Small edit to readme and clean up folders
    [Couvette Holder Lid.stl, Couvette Holder v20.f3z, Couvette Holder.stl, LDR holder.stl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]
2021-03-20 Added some calculations on LDR and resistor
